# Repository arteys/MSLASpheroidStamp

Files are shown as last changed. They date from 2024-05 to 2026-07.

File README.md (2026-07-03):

# MSLASpheroidStamp

# Introduction

Cell spheroids, everyone! Seriously, every cell biologist needs spheroids. It's fun and interesting. Okay, maybe not every one, but if you're reading this....
This project is about how you can use an MSLA 3d printer (and, in some cases) two-component silicone to make microwells in an agarose (or even agar) gel poured into a regular culture plastic. And we are not talking about some kind of multiphoton superprinter, the MSLA for $200 from the Amazon/Aliexpress/etc will work fine. 

I propose two approaches: to use silicone molds (molds for casting which can also be printed), in which agar is poured and further transferred into a tablet/flask, or to print a stamp, with which microwells are made directly in the gel poured into the dish/plate. 



Silicone mold for 6-well plates (A) and stamp for 96-well plates (B)

Of course I'm not the first to think of this, there's a preprint somewhere below where I've discussed quite a few similar options, including commercial MicroTissue (which cost some wild money for a piece of silicone). 

However, in the literature, the process of making such things is either terribly written, or the authors suggest using thousands of dollars worth of equipment. More often it is both. That's why I lay it all out in the form of protocols, as well as attach all the models. Including in FreeCAD format, offering those who wish to modify everything as you want and need. 



Microwells in a 96-well plate (A), glass-bottom dish mold for confocal microscopy (B), 6-well plate mold (C) and twin megamold for T-75 culture vials with 28564 microwells (D).

If everything is done correctly (and it's really not difficult) you can get such cuties as on the picture below. And then do all sorts of strange things with them. 


Spheroids made from cells of different cultures in microwells in the wells of a 96-well plate. Further they will be poisoned (at least some of them) with all sorts of poisons under the sound of laughter, as befits a mad scientist. 

# Files
Unfortunately the stl files are too big for github, so they are on [zenodo.com](https://zenodo.org/records/14562031) and on [Printables](https://www.printables.com/model/1243707-stamps-and-molds-for-mslaspheroidstamp)  

### Z-offset 

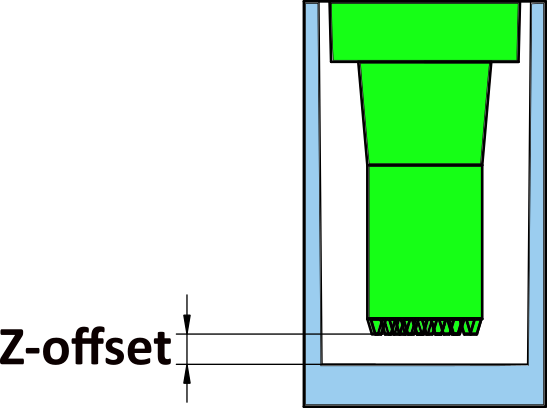
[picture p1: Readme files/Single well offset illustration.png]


The standards for culture plastic sizes are a joke. Especially for depth, so I attach stamp models with different z-offset to match to specific plates

# Molds

## 6-plate/dish microwell production

### Silicone Mold prodoctuion
#### The choice of silicone
This is the tricky part. Staying in the ideology of accessibility and DIY, I used the usual model two-component silicone available in the hobby store. Two-component platinum-based silicones definitely do not work - there is some kind of reaction between the silicone and the printed part and the silicone does not polymerize. Tin-based silicones remain, they generally work well. However, not all, I have met at least one that sticks to MSLA printed parts tightly and then it is impossible to separate the finished molds. Accordingly, if someone decides to make such molds, silicone will have to be selected empirically. And I didn't use any chemical separators because I didn't want to add their remnants to the biological medium.

#### Tools and equipment

- Vacuum chamber
- Two-component silicone (that you are sure about)
- Dye for silicone (with it is better to see how well mixed silicone, as well as you can use different colours for colour coding
- Disposable wooden or plastic spatulas.
- Wipes and gloves (this process will inevitably be messy)

#### Process
The total volume of silicone depends on how many molds you make at a time. Also silicone is quite hard to transfer quantitatively, it's a skill. Therefore, it is better to take with reserve. You will need two portions of silicone. The first portion is about ten grams per mold, the second twenty. 

1. Mix the first (smaller) portion of silicone with the hardener and dye 
2. Transfer to the molds and spread evenly with the spatula, making sure that the silicone covers the entire area evenly.
3. Transfer the molds to the vacuum chamber and evacuate, then let air in and evacuate again. Leave under vacuum for 3-5 minutes
4. Mix the second batch of silicone with hardener and dye (another colour can be used)
5. Release air, take the molds out of the vacuum chamber and pour the second portion of silicone into them
6. Remove the excess with a spatula
7. Leave for 24 hours (or as recommended by the silicone manufacturer) until curing

### Gel mold productuion
#### Before starting work
Nothing is sterile by default or even intended to be. In the laminar flow hood, it is highly recommended to treat the molds and stamps with 70% isopropyl or ethyl alcohol before the first use. You can use a spray bottle, but it is better to treat them by immersing them in a alcohol for a few minutes. 
I would not advise autoclaving, and molds and stamps, in principle, should withstand such treatment, but without guarantees. 
It is most convenient to store it in the box of tips, this box can also be treated with alcohol and stored inside the laminar flow hood while working. 

#### Tools and equipment

- Laminar flow hood
- Microwave or other way to melt the gel
- Molds
- Plastic pasteur pipettes (2-5 ml)
- Tips for 10-200 ul pipette
- Agar/agarose solution with a concentration of about 1-3% mass. The minimum volume required per plate is about 5 ml, but it is better to melt 10-20 so that the melted gel in the bath does not solidify so quickly.

#### Process
1.	Melt the agar/agarose solution, preferably bring to a boil 
2.	Using a paster pipette, transfer the gel to the silicone molds, spreading it gently over the surface, large bubbles can be sucked up with the pipette
3. If you use a silicone mold with a small size of micropins (300 um), air bubbles often get stuck on them, which spoil the agarose mold. To get rid of them mold should be ‘ironed’ for example with a 10-200 tip (Watch the video below). 
4. Agarose hardens for 10-20 minutes, after which the mold can be carefully removed from the mold and transferred to a plate cell 6-well plate cell or a suitable dish.
5.	Agarose molds are ready for cell seeding

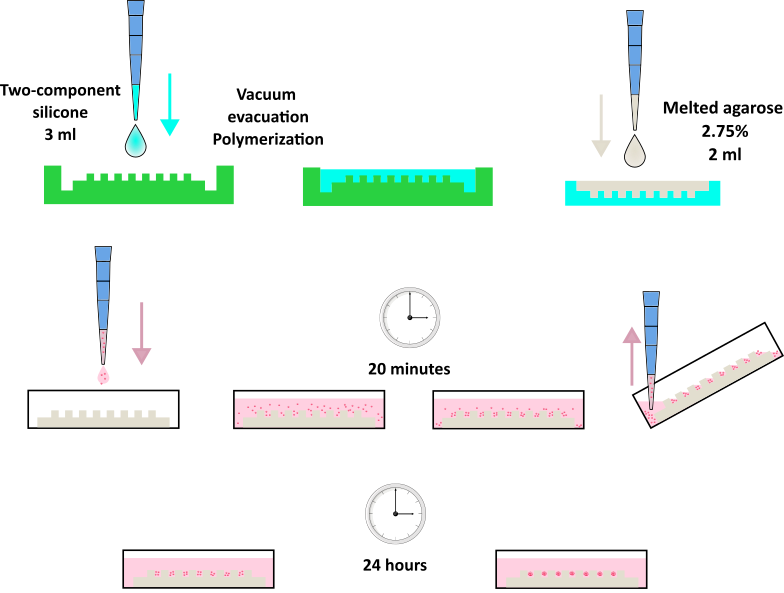
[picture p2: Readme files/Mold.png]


https://github.com/user-attachments/assets/4c41e45f-066e-499b-a9de-289ee6c0a233

_Process of filling mold with agarose_

https://github.com/user-attachments/assets/55440b95-25c6-4f36-a674-90fb6afe1f3b

_Process of removing bubbles from the mold_

https://github.com/user-attachments/assets/c4b449f8-795c-471a-a6a9-0f1629ddc110

_Extracting of the agarose mold_

#### Cell seeding
1.  Detach the cells using the laboratory procedure. 
2.	Count the cells in suspension and dilute to the required number per microwell. About 300 µl can be poured into the recess of the agarose mold. 
3.	Transfer the cell suspension into the recess of the mold
4.	Allow 15-30 minutes for the cells to settle under gravity.
5.	Tilt the plate with molds and carefully remove the medium with excess cells that did not fall into the wells
6.	Add fresh medium, including the empty space around the mold.
7.	Place the plates in the incubator until the spheroids consolidate for 24 hours

## Stamps

### 96-plate microwell production

#### Before starting work
Nothing is sterile by default or even intended to be. In the laminar flow hood, it is highly recommended to treat the molds and stamps with 70% isopropyl or ethyl alcohol before the first use. You can use a spray bottle, but it is better to treat them by immersing them in a alcohol for a few minutes. 
I would not advise autoclaving, and molds and stamps, in principle, should withstand such treatment, but without guarantees. 
It is most convenient to store it in the box of tips, this box can also be treated with alcohol and stored inside the laminar flow hood while working. 

#### Tools and equipment

- Laminar flow hood
- Microwave or other way to melt the gel
- Stamps - 6 pieces
- Multichannel pipette (capable of dispensing 50 µl of liquid) - 1 piece
- Tub for multichannel pipette
- Tips for pipette
- 96-well plate  
- Agar/agarose solution with a concentration of about 1-3% mass. The minimum volume required per plate is about 5 ml, but it is better to melt 10-20 so that the melted gel in the bath does not solidify so quickly.

#### Process

Working with molten agar/agarose requires care and, more importantly, speed, so it is better to prepare everything within reach in advance
1. Set the pipette to 50 µl 
2.	Melt the agar/agarose solution, preferably bring it to a boil 
3.	In a laminar flow hood, pour the agarose into the tub for the multichannel pipette
4.	Use the pipette to transfer 50 µl into the two columns of the plate and immediately place a stamp in these columns. Make sure that the stamp is fully inserted (there is a tab on it centring it in the well, make sure it is inserted). It is necessary to do everything as quickly as possible, so that the gel does not freeze in the spouts of the dispenser
5.	Pour two more columns, set the stamp, repeat until all the stamps are installed 
6.	Wait for the gel to solidify (10-15 minutes, depending on agar/agarose and room temperature)
7.	Remove the stamps. This is the most critical step. It is most convenient to turn the plates with the short part towards yourself and remove the stamps with two hands from the sides. Gently rock the stamp back and forth before removal. If the gel concentration is optimal and the gel is fully cured, the stamp should come out clean and free of gel pieces and the microwells should remain intact inside the tablet. A few wells per plate usually come with bubbles, it's a matter of luck and it's hard to do anything about it. A video of the extraction process is shown below
8.	The microwells are ready for seeding of cells

https://github.com/arteys/MSLASpheroidStamp/assets/7783671/63acb3b1-17a5-44c3-86e2-7b8f0d8d8371

_Process of extracting the stamp from the plate_

#### Cell seeding

Before conducting a serious experiment, it is best to determine the optimal number of cells needed to form spheroids. They should not be too many or the extra cells in the well will form spheroids of uncontrolled size outside the microwells. The figure below shows spheroids formed from HeLa with different numbers of cells per cell. In this case about 1000-500 cells per microwell is optimal, when dense spheroids are formed after a day and there are practically no cells outside the cells. 

You will need standard equipment and supplies for working with cell cultures, as well as a microwell plate made in the previous step, and:
- Centrifuge or vortex with a plate rotor (optional)

1. Detach the cells using the laboratory procedure.  
2.	Count the cells in suspension and dilute to the required number per microwell. One plate well can be filled with 50 - 100 µl of medium. 
3.	Transfer the cell suspension to the tub for the multichannel pipette
4.	Using the multi-channel pipette, transfer the cell suspension into the plate
5.	Either centrifuge at minimum speed to allow the cells to settle to the bottom of the microwells or hold the plates for 15-30 minutes to allow the cells to settle by gravity.
6.	Some cells are deposited between the cells or above or at the top of the plate cell where the stamp entered the agarose. To remove excess cells the plate should be tilted at 45 degrees and carefully remove the medium with excess cells with a multichannel pipette, pipetting several times.   
7.	50-100 µl of new medium can be poured in place of the removed medium 
8.	Place the plates in the incubator until the spheroids consolidate for 24 hours

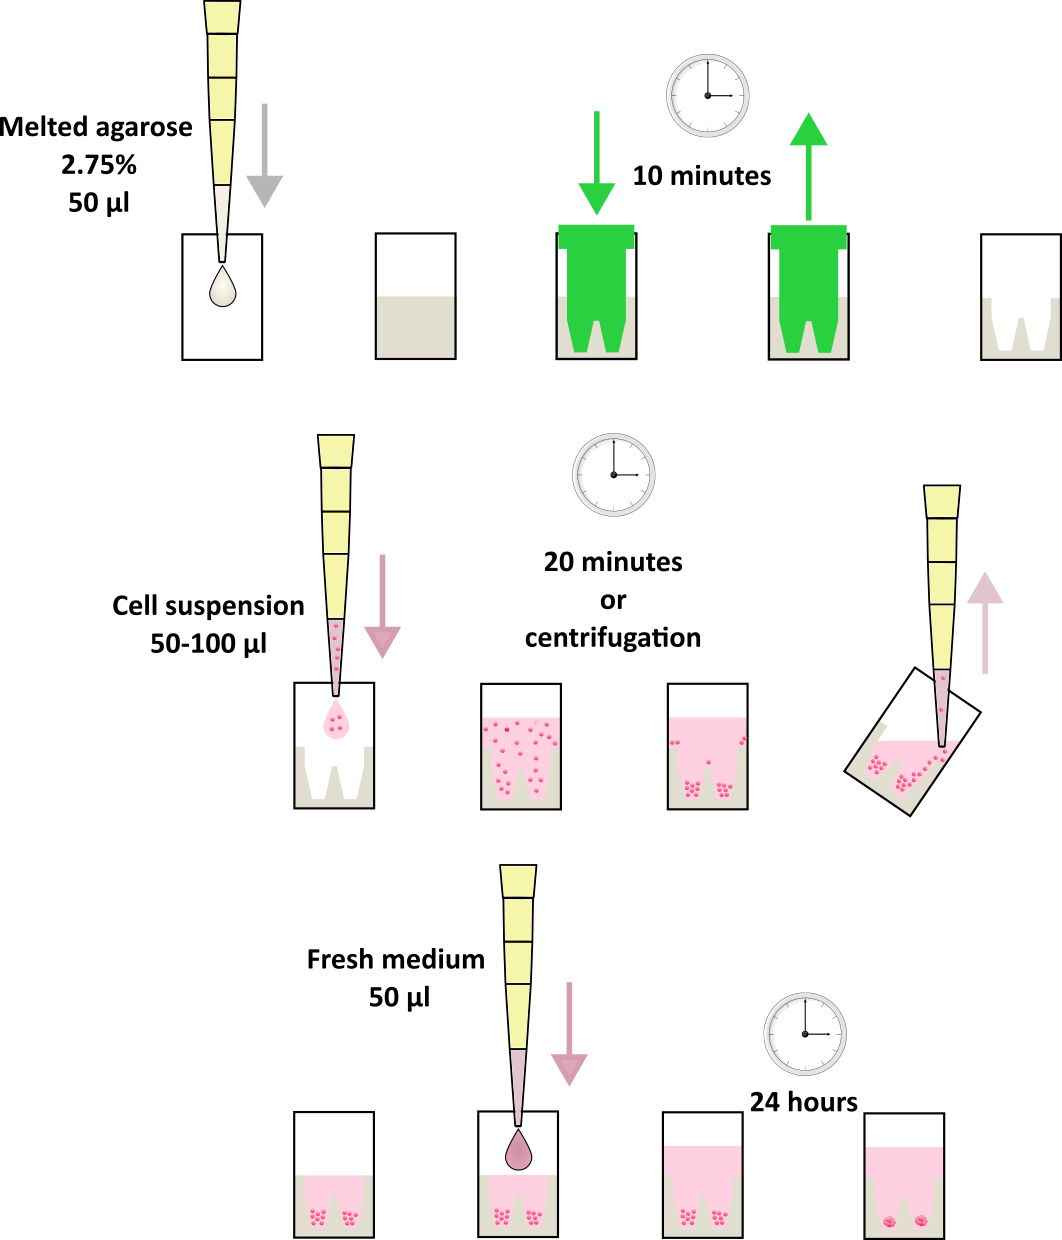
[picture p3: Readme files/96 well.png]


### Glass bottom dish microwell production

#### Before starting work
Nothing is sterile by default or even intended to be. In the laminar flow hood, it is highly recommended to treat the molds and stamps with 70% isopropyl or ethyl alcohol before the first use. You can use a spray bottle, but it is better to treat them by immersing them in a alcohol for a few minutes. 
I would not advise autoclaving, and molds and stamps, in principle, should withstand such treatment, but without guarantees. 
It is most convenient to store it in the box of tips, this box can also be treated with alcohol and stored inside the laminar flow hood while working. 

#### Tools and equipment

- Laminar flow hood
- Microwave or other way to melt the gel
- Stamps
- Plastic pasteur pipettes (2-5 ml)
- Tips for pipette
- Glass bottom dishes plate  
- Agar/agarose solution with a concentration of about 1-3% mass. The minimum volume required per dish is about 1 ml, but it is better to melt 10-20 so that the melted gel in the bath does not solidify so quickly.

#### Process

Working with molten agar/agarose requires care and, more importantly, speed, so it is better to prepare everything within reach in advance
1.	Melt the agar/agarose solution, preferably bring it to a boil 
2.	In a laminar flow hood, pour the agarose into the tub for the multichannel pipette
3.	Use the pipette to transfer 1-2 ml into the dish of the plate and immediately insert a stamp. Make sure that the stamp is fully inserted (there is a tab on it centring it in the well, make sure it is inserted)
4.	Wait for the gel to solidify (10-15 minutes, depending on agar/agarose and room temperature)
5.	Remove the stamp. 
6.	The microwells are ready for seeding of cells

#### Cell seeding

Before conducting a serious experiment, it is best to determine the optimal number of cells needed to form spheroids. They should not be too many or the extra cells in the well will form spheroids of uncontrolled size outside the microwells. The figure below shows spheroids formed from HeLa with different numbers of cells per cell. In this case about 1000-500 cells per microwell is optimal, when dense spheroids are formed after a day and there are practically no cells outside the cells. 

You will need standard equipment and supplies for working with cell cultures, as well as a microwell plate made in the previous step, and:
- Centrifuge or vortex with a plate rotor (optional)

1. Detach the cells using the laboratory procedure.  
2.	Count the cells in suspension and dilute to the required number per microwell. One dish can be filled with 200 - 400 µl of medium. 
3.	Using the pipette, transfer the cell suspension into the plate
4.	Place the dishes in the incubator until the spheroids consolidate for 24 hours

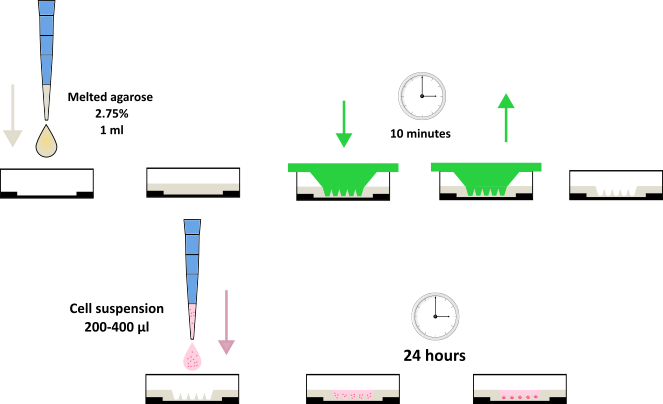
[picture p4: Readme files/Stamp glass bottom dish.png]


# Reproducibility
Of course it would be ridiculous to say much about the reproducibility of my methodology, but not to test it. So scientists in other laboratories (not affiliated with the authors of the study), having received stamps, silicone molds and instructions, were able to reproduce the process of stamp printing and spheroids manufacturing. They used other cell cultures, laboratory plastic from other manufacturers, as well as agar and agarose of other brands. Instructions as well as 3d models are available on the project page on GitHub and in the supplement materials

#  Reference
Preprint: https://www.biorxiv.org/content/10.1101/2024.05.12.593682v2

Paper: https://www.sciencedirect.com/science/article/pii/S2405886625000326?dgcid=author

# Featured in
https://doi.org/10.3390/md23090353

https://doi.org/10.3390/md23120456

https://doi.org/10.1088/1758-5090/ae63f9

https://doi.org/10.1134/S0006297926600286

# Acknolegments
For testing our methodology and proving its reproducibility, I am grateful to
Anatoliy Zubritskiy from FRC "Fundamentals for Biotechnology" RAS (Moscow, Russia),
Kuzmich Alexandra and Yurchenko Ekaterina from Pacific Institute of Bioorganic Chemistry
RAS (Vladivostok, Russia), Alexandra Dalina from Engelhardt Institute of Molecular Biology
RAS (Moscow, Russia) and Saida Karshieva from National University of Science and
Technology MISIS (Moscow, Russia)

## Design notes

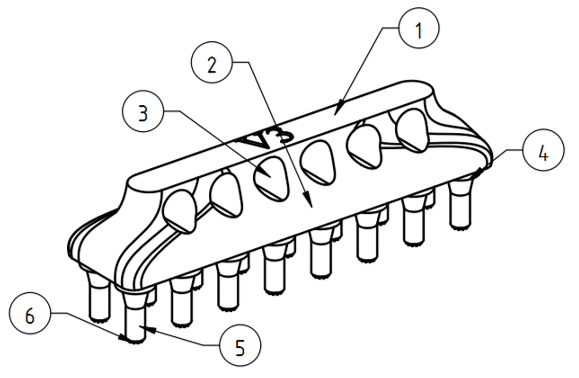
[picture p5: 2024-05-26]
Readme files/96 well stamp sketch.png

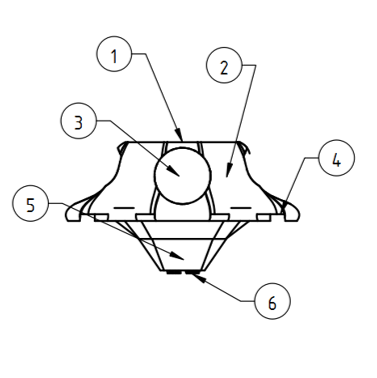
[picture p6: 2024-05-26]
Readme files/Petri dish stamp sketch.png

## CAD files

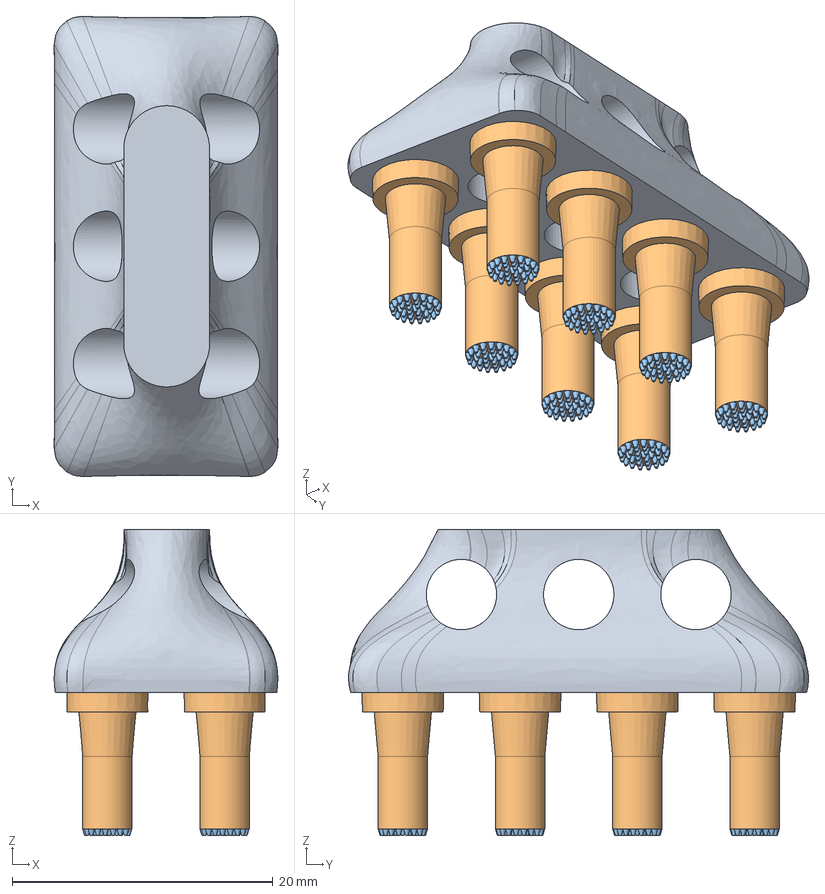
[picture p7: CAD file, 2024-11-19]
3d moldes/96 well micro z=1.step
17.2 x 35.3 x 23.5 mm

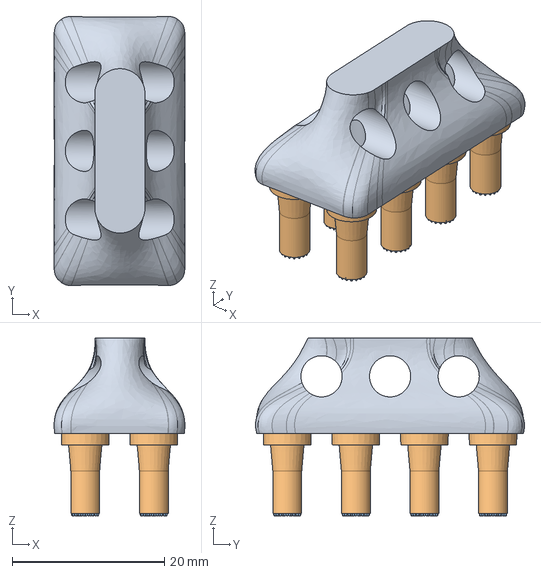
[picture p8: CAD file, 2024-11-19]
3d moldes/96 well micro z=1_2.step
17.2 x 35.3 x 23.3 mm

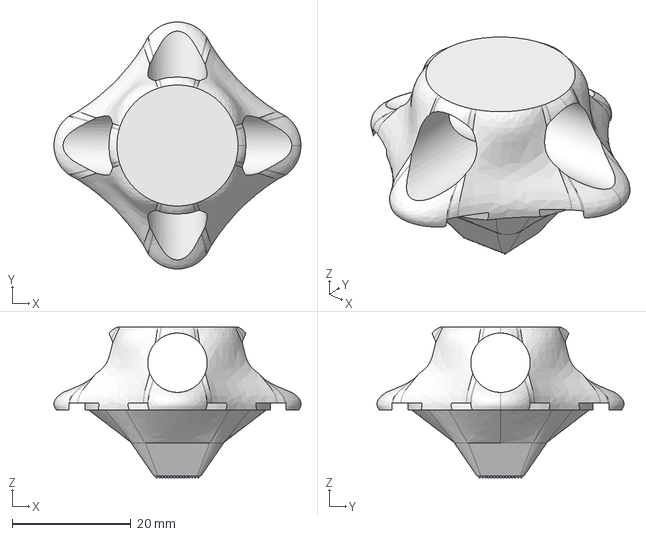
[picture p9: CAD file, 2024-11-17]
3d moldes/Glass bottom dish stamp release.FCStd
41.6 x 41.6 x 25.4 mm

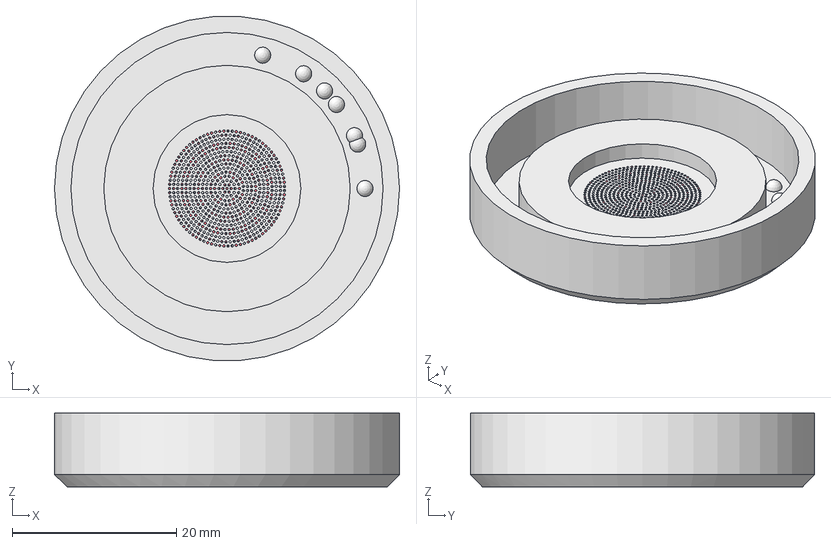
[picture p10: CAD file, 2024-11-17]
3d moldes/6 well mold release.FCStd
42.0 x 41.9 x 9.00 mm
500 um 410N mold
300 um 653N mold

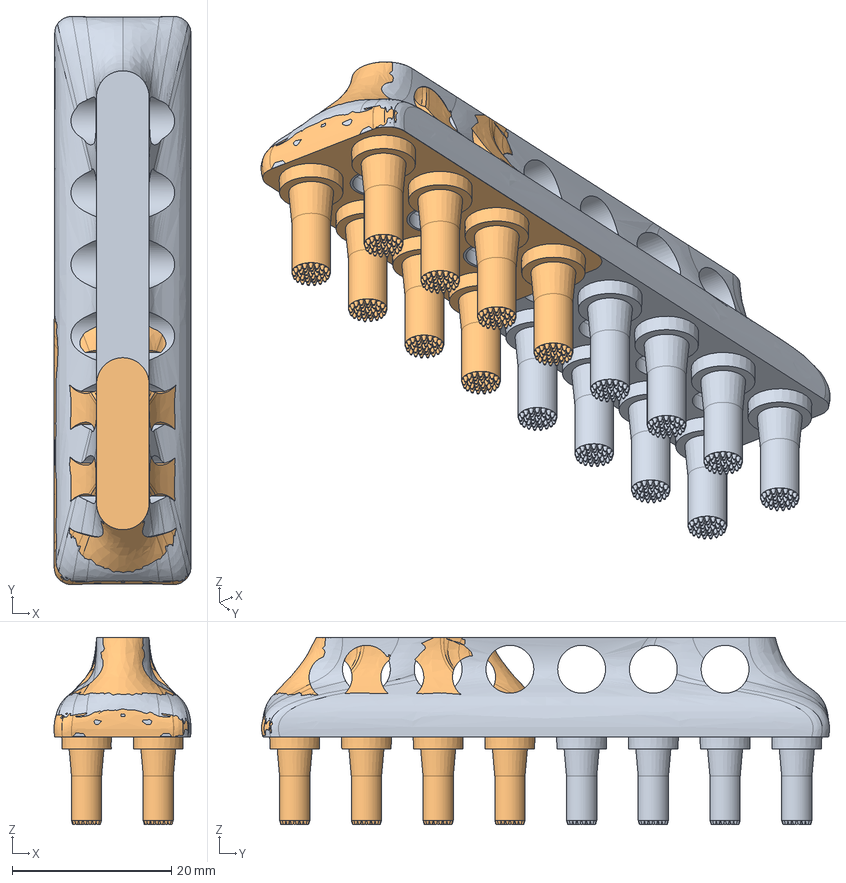
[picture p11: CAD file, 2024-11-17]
3d moldes/96 well release.FCStd
17.2 x 71.3 x 23.5 mm
96 well basic
96 well micro

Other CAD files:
3d moldes/96 well micro z=0_8.step

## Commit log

2024-05-12 Add model files
    [6 well molds.FCStd, 96 well stamp.FCStd, Glass bottom petri dish stamp (cylinder).FCStd, Glass bottom petri dish stamp (test).FCStd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]
2024-10-27 Update README.md
    Instructuional video about molds
2024-10-27 Add files via upload
    Instructuioanl Images for mold and stamps
2024-10-27 Update README.md
    Instruction images for mold and 96-well
2024-10-27 Add files via upload
    Missed assets in mold image
2024-10-27 Update README.md
    Mold extracting video
2024-11-17 Delete 3d models directory
    It is easer than delete one by one
    [6 well molds.FCStd, 96 well stamp.FCStd, Glass bottom petri dish stamp (cylinder).FCStd, Glass bottom petri dish stamp (test).FCStd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]
2024-11-17 freeCAD files for 96 well stamps
    [96 well v4 realise.FCStd]
2024-11-17 96 well and 6 well freeCAD files
    [6 well mold release.FCStd, 96 well release.FCStd]
2024-11-17 Add files via upload
    Some .step
    [96 well micro z=0_8.step]
2024-11-19 More step files
    [96 well micro z=1.step, 96 well micro z=1_2.step]
2025-03-26 Update README.md
    Link to printables
